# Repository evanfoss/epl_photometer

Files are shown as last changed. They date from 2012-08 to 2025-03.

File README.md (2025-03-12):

# EPL Photometer

By Evan Foss

Date 2011.10.05 (YYYY.MM.DD)

Documentation reuploaded 2025.03.12 by EEF

## Project Description

This project is a photometer, unlike a conventional light meter it is designed to take readings of a stroboscopic light source. It is compact and shielded enough to put in a chamber and operate continuously. It is not meant for perfect for any application because of the limitations in it's response to specific wavelengths and in calibration. It is made with the best matched photodiodes available in our price range. It is also limited in that do to our inability to develop a good reference for single wavelength calibration the device is only good for qualitative (relative) measurements not quantitative measurements. We are working to rectify this last limitation but there is no telling how long it will take to find an adequate calibration method.

# Development

## Toolchain

The development toolchain was as follows:

|Tool Name             | License        | Function
|:---------------      | :------------- | :-----------------
|<a href="https://www.sagemath.org/">SageMath</a>                                            | Open Source       | Scientific Programming Language used for calculations
|<a href="https://github.com/lepton-eda/lepton-eda">lepton-eda</a>                           | Open Source       | EDA (Electronic Design Automation) suite lepton-eda a fork of gEDA
|<a href="http://repo.hu/projects/pcb-rnd/">pcb-rnd</a>                                      | Open Source       | CAD (Computer Aided Design) tool for PCB (Printed Circuit Board) layout gEDA/PCB
|<a href="https://gerbv.github.io/">gerbv</a>                                                | Open Source       | Gerber viewer
|<a href="https://www.gnu.org/software/make/">GNU/Make</a>                                   | Open Source       | Toolchain automation

The project was originally designed using gEDA but Lepton-EDA is backward compatible to it. Like wise the original PCB artwork was designed in gEDA/PCB which was also forked to create pcb-rnd which is also backward compatible.

For the math I was doing I suggest migrating off SageMath to <a href="https://octave.org/">Octave</a> as Sagemath maintence for work this simple is excessive.

## Organization

|File Name/Directory            | Description
|:---------------               |:---------------
|4alberta	                    | The files for the LT1793-sheilded version of the board.
|README.md		                | This file.
|datasheets		                | The data sheets for the various parts used/(considered for use) in the project.
|lt1793-sheilded		        | The 1st production version of the device using an LT1793 for the transimpedance amplifier and a shield using 0.1" spaced headers.
|lt1793-unsheilded	            | The pre-production version of the device using an LT1793 for the transimpedance amplifier minus the shield.
|ltc6240			            | The pre-production version of the device using an LTC6240 for the transimpedance amplifier for higher frequency responce. This design is incomplete.
|math                           | The scripts and calculations used for the design of the device.

## Design

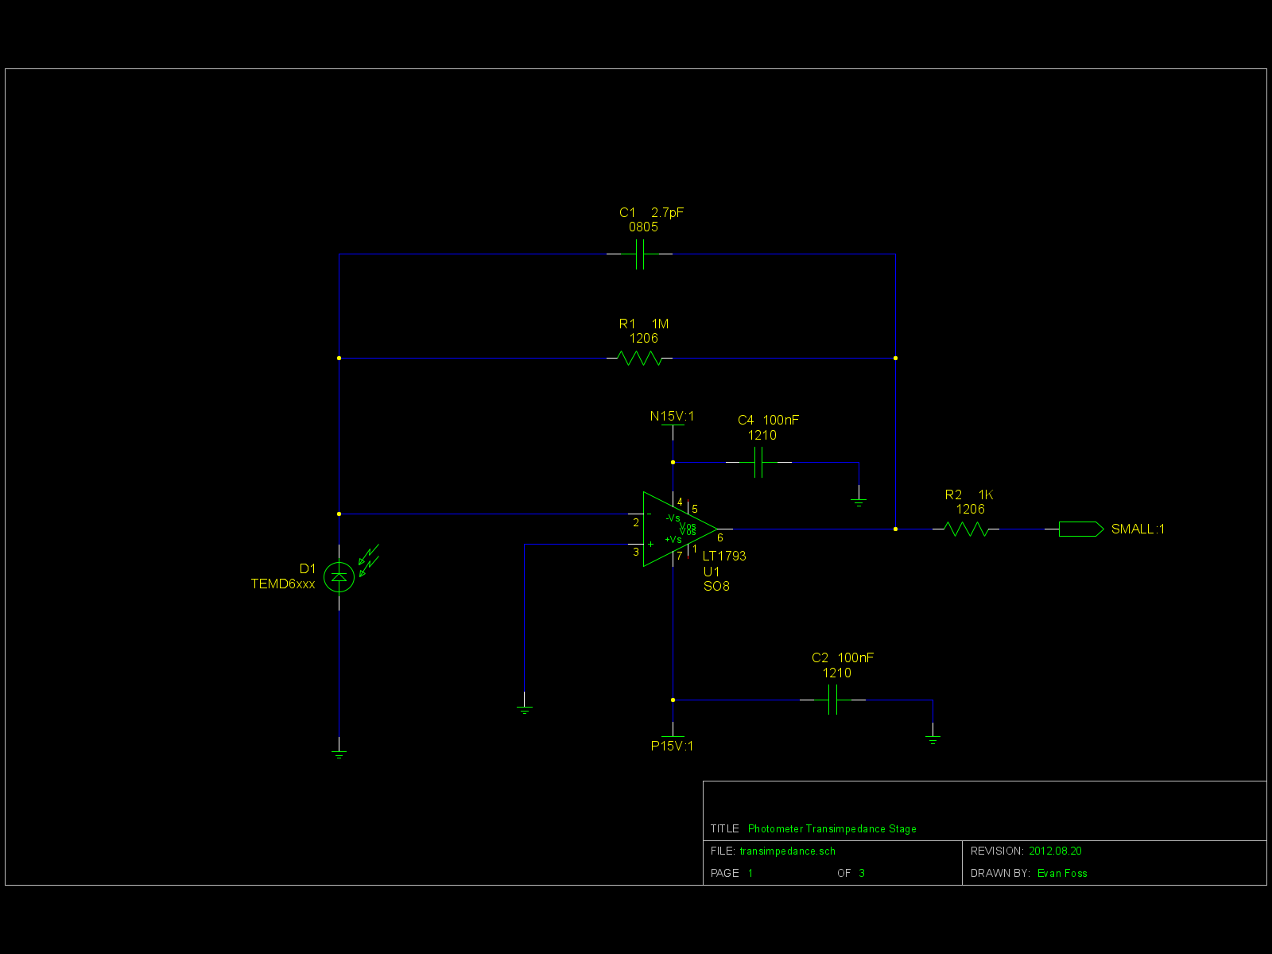
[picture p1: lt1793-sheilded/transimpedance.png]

The photometer uses a photodiode to convert illumination into an electrical current. The current is amplified by a transimpedance stage converting it to a voltage. The voltage is then amplified by a second amplifier that is also capable of driving the capacitive load from the BNC cable. Ideally all the gain would take place in one stage but that is not possible because of real world limitations on the size of the feedback resistor, input capacitance, amplifier stability and etc. More on this will be explained later.

The input diode was selected because it had response in the relevant areas. Many diodes were considered but the TEMD6010FX1 was selected because it had some response in the shorter wavelengths and because it had relatively low capacitance. There were other diodes with more appropriate response but they were all unobtanium because of the minimum quantity required. To carry the project forward we have to assume some things about what the maximum and typical levels of illumination will be. With the amount of illumination the amount of current can be used to work out the required amount of gain for the rest of the device.

The feedback resistor on the transimpedance stage is not large enough on it's own so a second stage is required. The LT1793 was chosen for the transimpedance stage because it has reasonably low input current bias and input current offset which are better for obvious reasons. The LT1793 also has a low input capacitance which is important for stability and just to finish off it has a reasonable gain band width product. For higher bandwidths the LTC6240 was considered but do not need the bandwidth yet. While it is possible to make a larger resistance it would not work because the minor capacitance across the pads of the resistors footprint will be large enough to limit total feedback impedance as frequency increases. While some feedback capacitance is good for compensating the amplifier the effect would be excess role off.

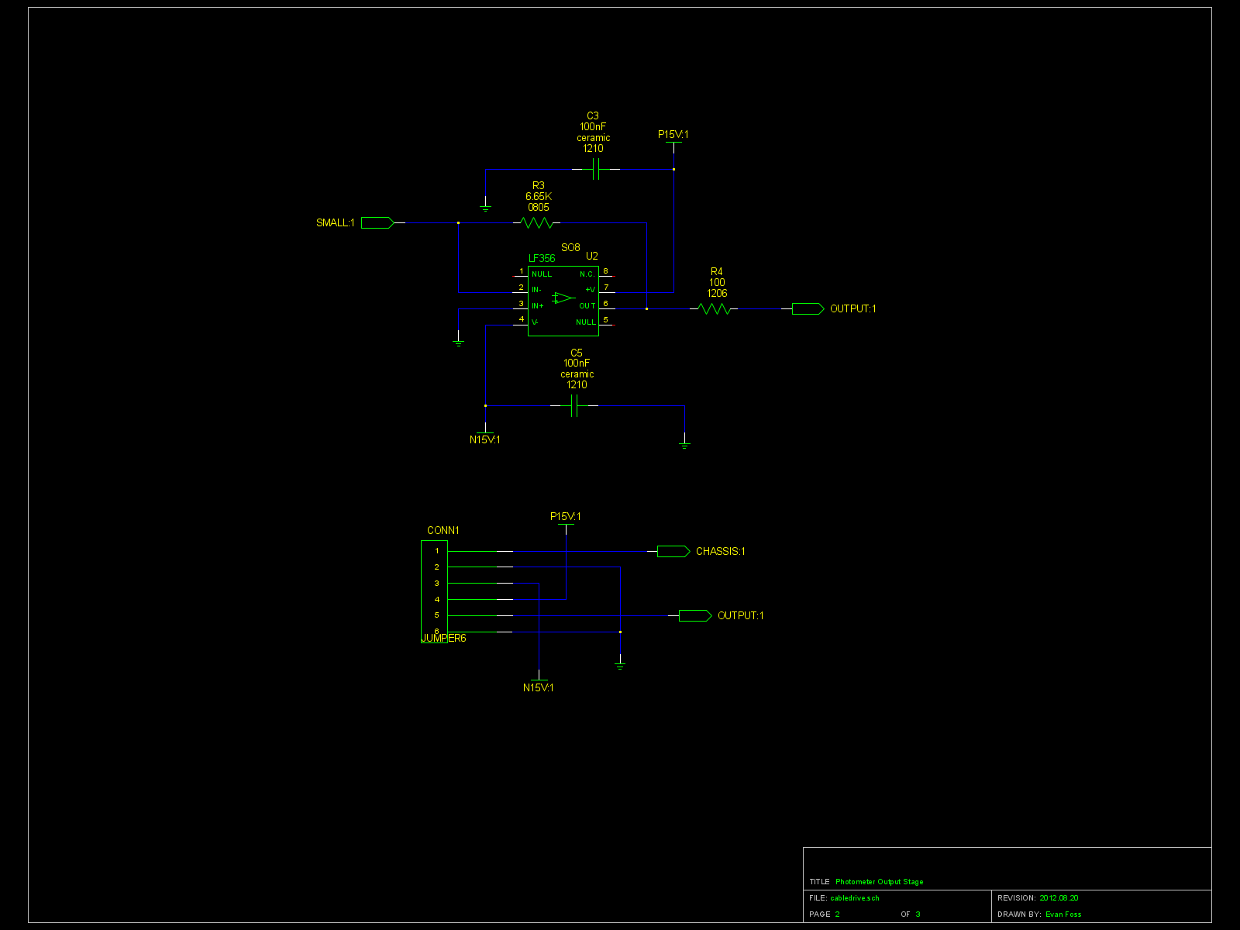
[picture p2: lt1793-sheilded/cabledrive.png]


The second stage is really just meant to pick up the slack from the transimpedance stage and driving the capacitive load of the output cable. It is the ability to drive a capacitive load that is why the LF356 was selected over any number of otherwise comparable amplifiers. The input resistance for the LF356 was selected because it was a reasonable margin from the output current of the LT1793. The math included in the project also checks if there should be a feedback capacitor on the second stage amplifier. It is highly unlikely to be needed.

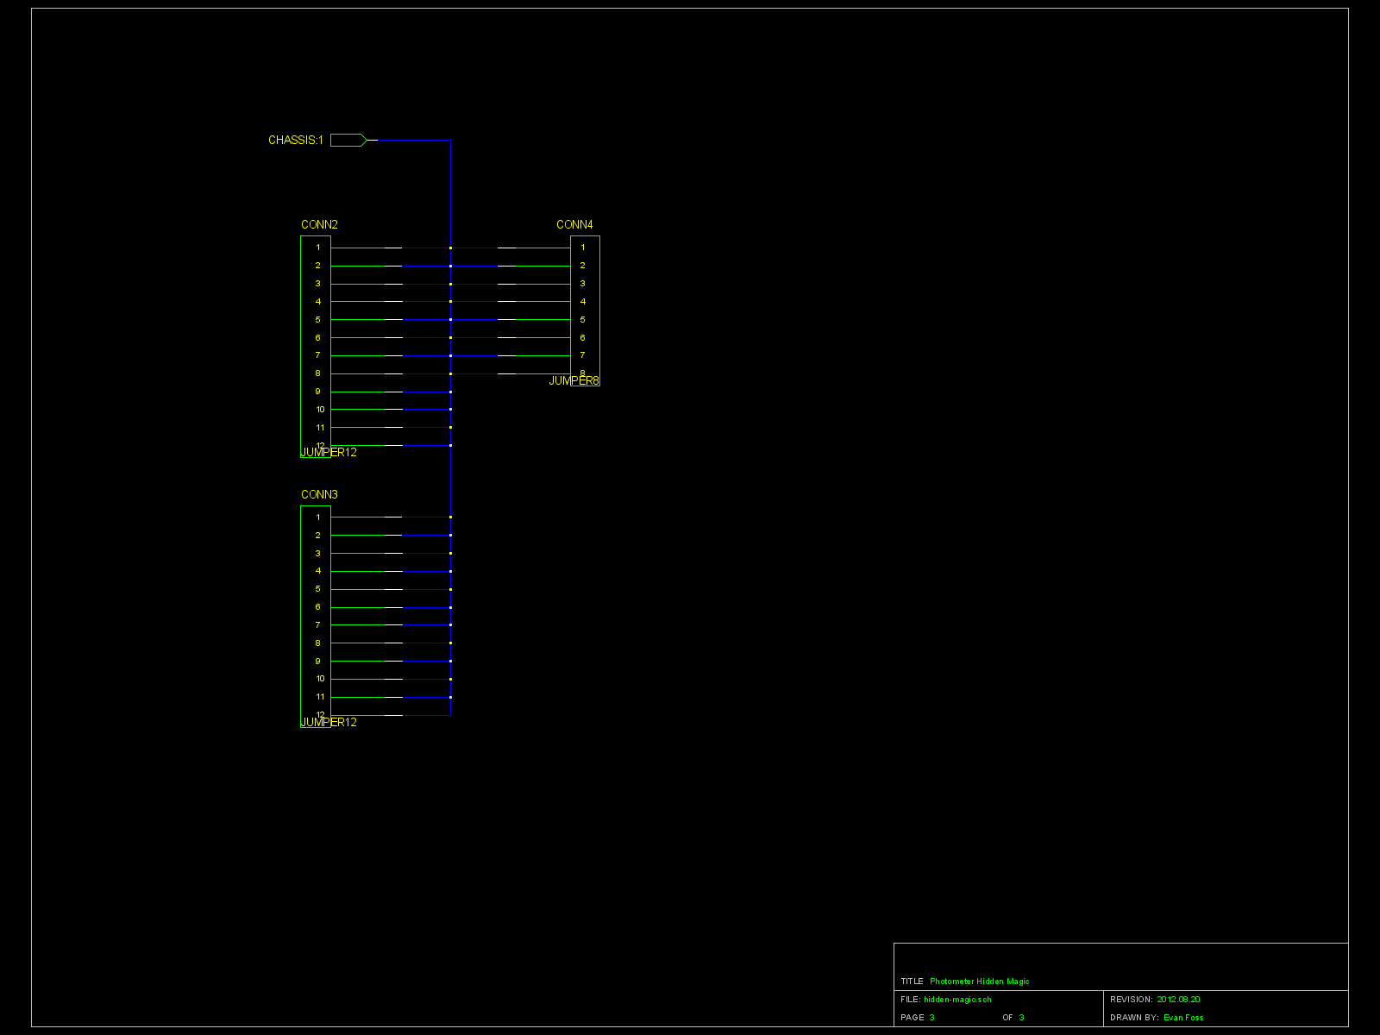
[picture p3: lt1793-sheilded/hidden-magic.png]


This is just the shielding for the device. Transimpedance amplifiers are very noise sensitive.

# Construction

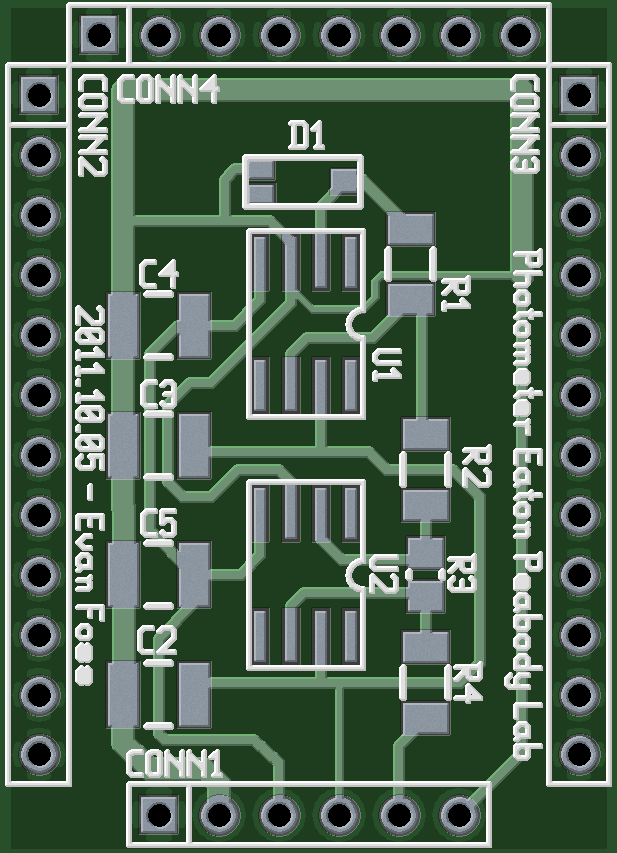
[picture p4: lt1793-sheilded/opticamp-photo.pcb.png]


The construction of the photometer seems straight forward until you consider the troubles of making it compact with only 2 layers for cost reasons and only 1 layer used for the design because the bottom is going to be used as part of the shield. The whole design except for the connector and the shield is done in SMT. 

Doing the shield in SMT was considered but that would have meant using a sheet of brass or copper and soldering it directly to the back layer of the board. While this is possible it would make rework on the board difficult and it would put considerable thermal stress on the board. The pads such a shield would have needed would have been of considerable size and the heat used to solder them might have cause them to delaminate off the board substraight. The  photodiode needs to be exposed for the best results but it also must be on the board to reduce capacitance so there is a whole in the shield. It has been our experience that holes attract all manner of unwanted contaminants so the shield needs to be removable for cleaning. It adds a considerable mount of bulk but 0.100” headers are used to connect the shield to the board. The shield being a piece of perforated board with a ground plane on it soldered to the headers.

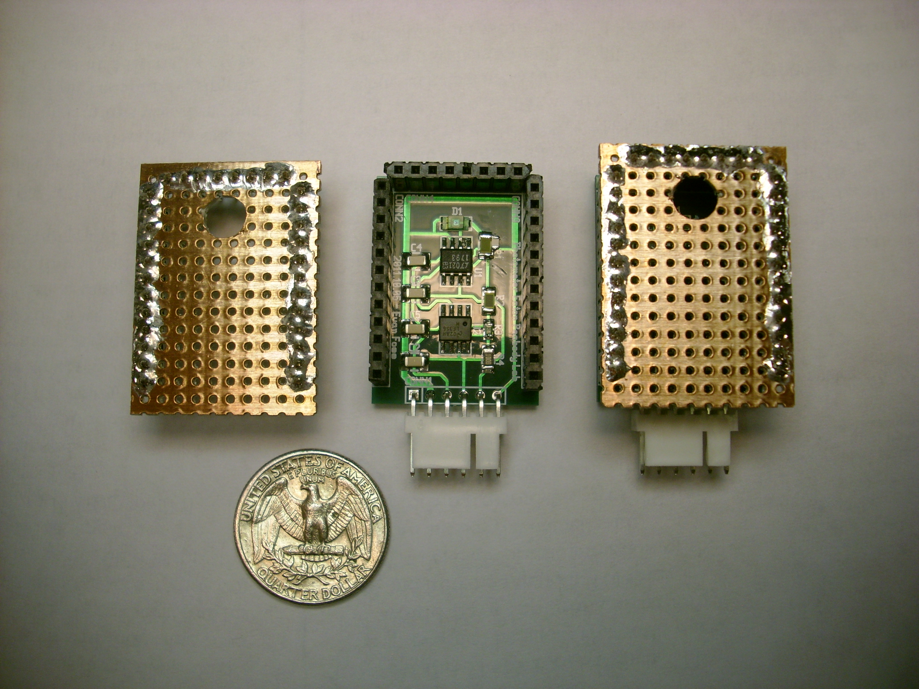
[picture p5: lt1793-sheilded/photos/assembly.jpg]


While the space between the transimpedance amplifier and the output stage amplifier is not that critical many other areas are very tightly controlled. The space between the photodiode and the trans-impedance amplifier should be as short as possible to reduce trace capacitance. The distance between the feedback resistors and their accompanying amplifiers also have to be kept short. The input resistor on the output amplifier is not very controlled and given the small size of the whole space the distance between the decoupling capacitors and everything else is also with in reason not critical. 

Making the connector in SMT was considered but having the connector pins go threw the board helps mechanically if the connector sees excess torc which can happen. The downside is of course that those points are exposed to the outside and could introduce noise but if this is a problem a small bit of adhesive backed copper foil can be put over the clip side of the connector or indeed the whole mating area.

To get from the connector on the photometer to the rest of the world there are two different methods. In a chamber the device uses a shielded cable carrying both the power and signal lines to an PCB with and edge card connector. The edge card supplies power from our standard EPL configuration of the EFP series vector subrack. The signal comes out of that same board via a right angle BNC connector. In the second configuration we use two shielded cables on going to a MiniHEX9 for power and the other to a BNC connector for the signal output. Because of the outside of the BNC cable being only at analog ground and not at shield potential this version is not suitable for use in a chamber.

# Validation

The photometer was tested for it's frequency reponse, noise floor, and linearity.

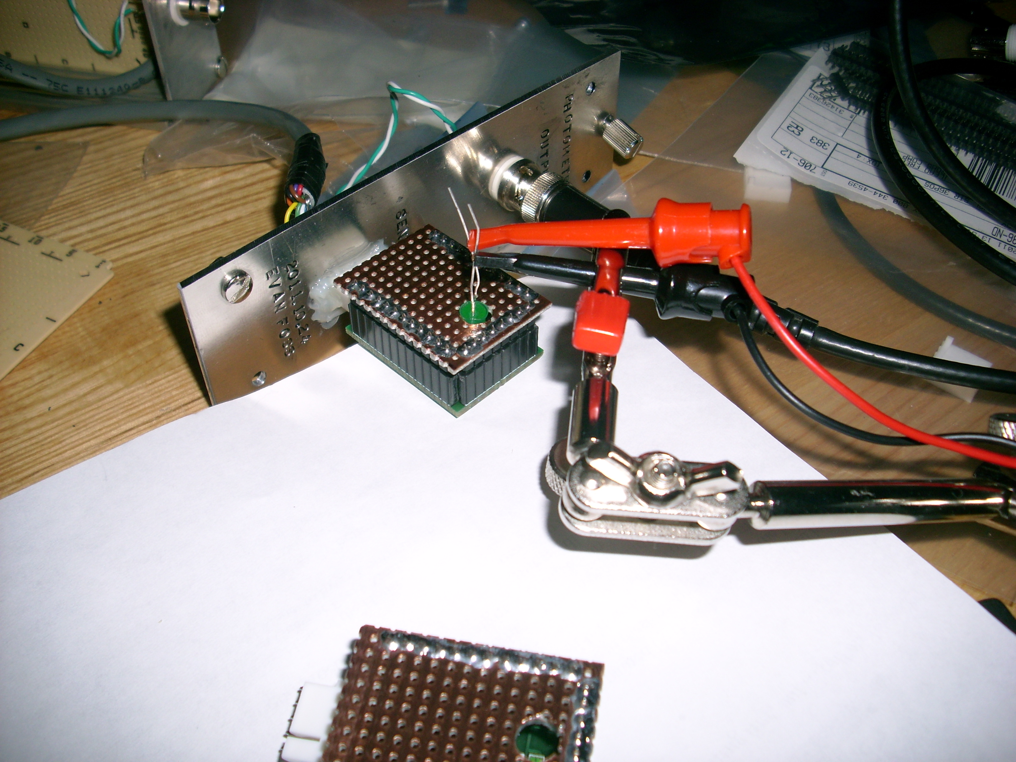
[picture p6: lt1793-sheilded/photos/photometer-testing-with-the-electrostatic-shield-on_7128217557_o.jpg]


For more on that testing data reach out to who ever has my lab notebook now.

|Generator used|Fall Time|Rise Time|Linearity
|:---------------|:---------------|:---------------|:---------------
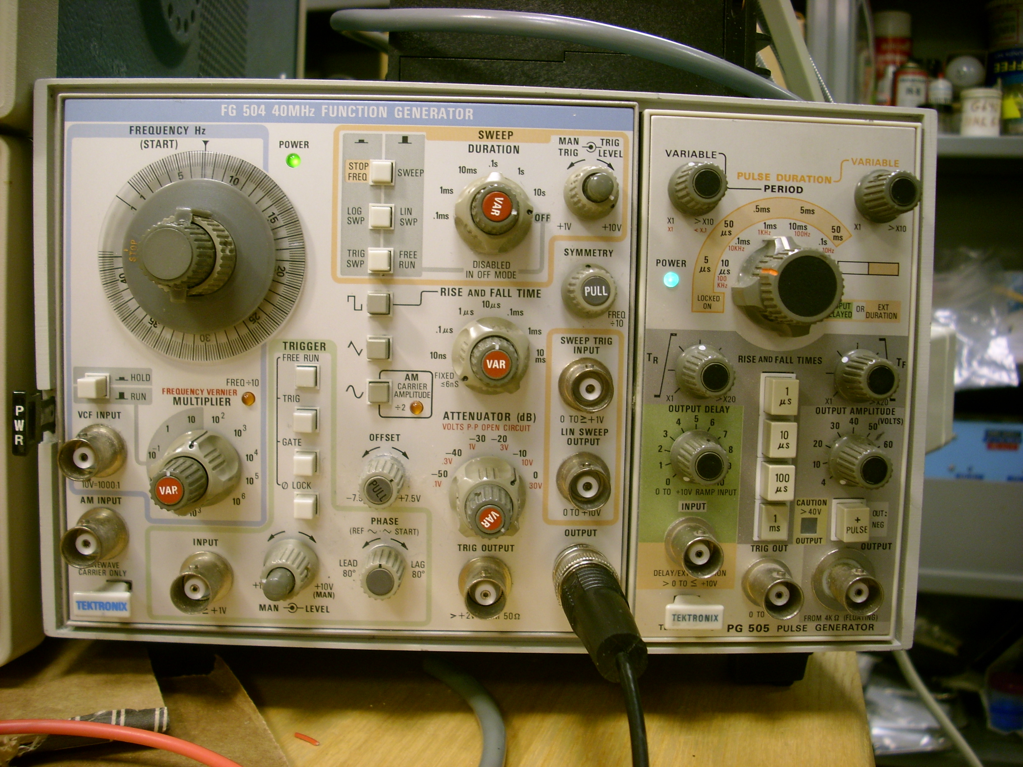
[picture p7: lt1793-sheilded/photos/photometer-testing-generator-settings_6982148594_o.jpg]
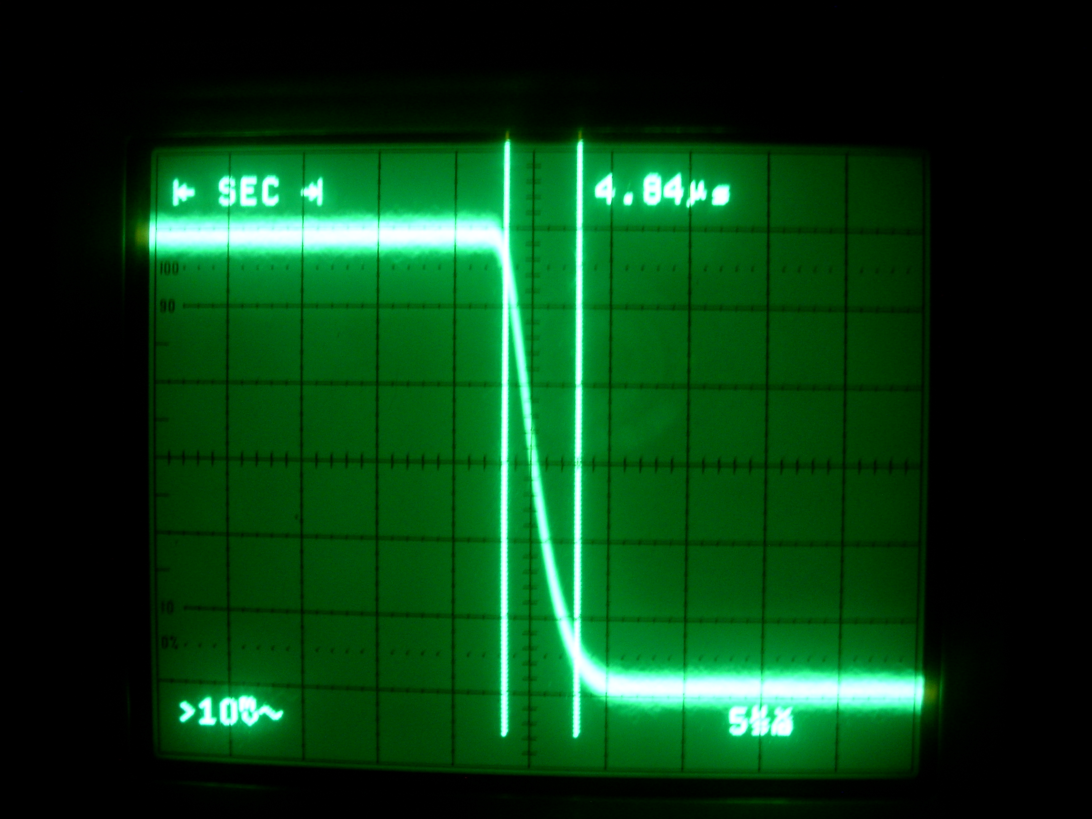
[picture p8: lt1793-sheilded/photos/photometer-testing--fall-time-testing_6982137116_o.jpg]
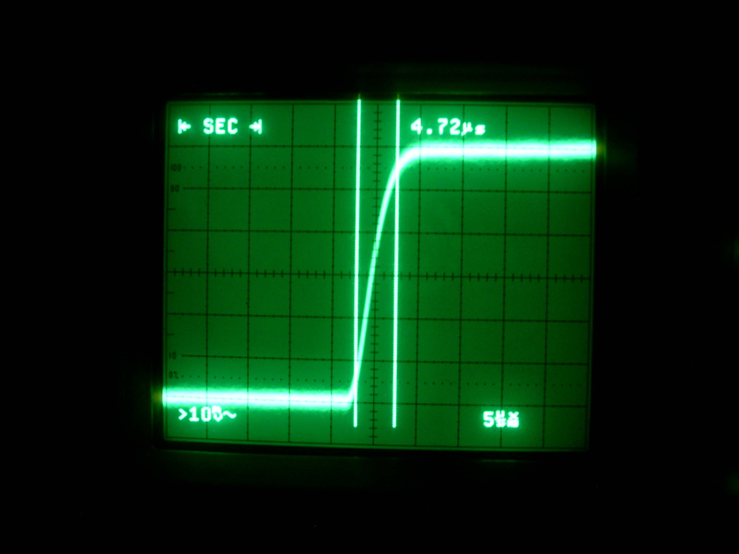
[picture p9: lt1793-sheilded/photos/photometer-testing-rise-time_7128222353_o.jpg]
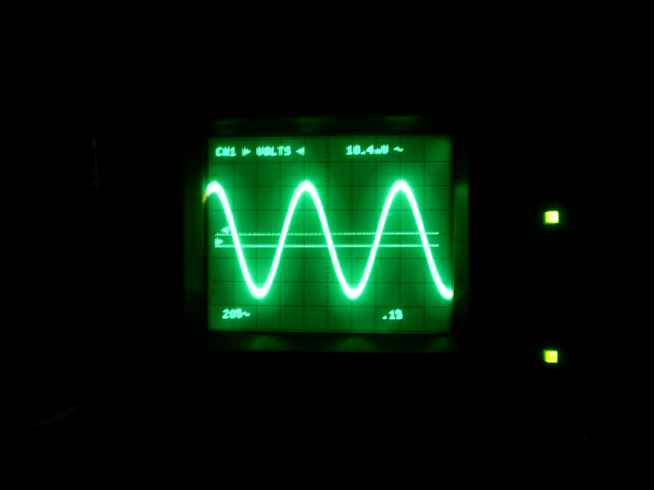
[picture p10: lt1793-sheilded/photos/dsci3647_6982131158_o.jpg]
||||

# Future

We only have to needs from this device that are unfulfilled. First we would like to be able calibrate it to a source of a known wavelength and power. Second it would be nice if it could have a better response at smaller wavelengths. Sadly we do not have the resources at this point but that may change later.

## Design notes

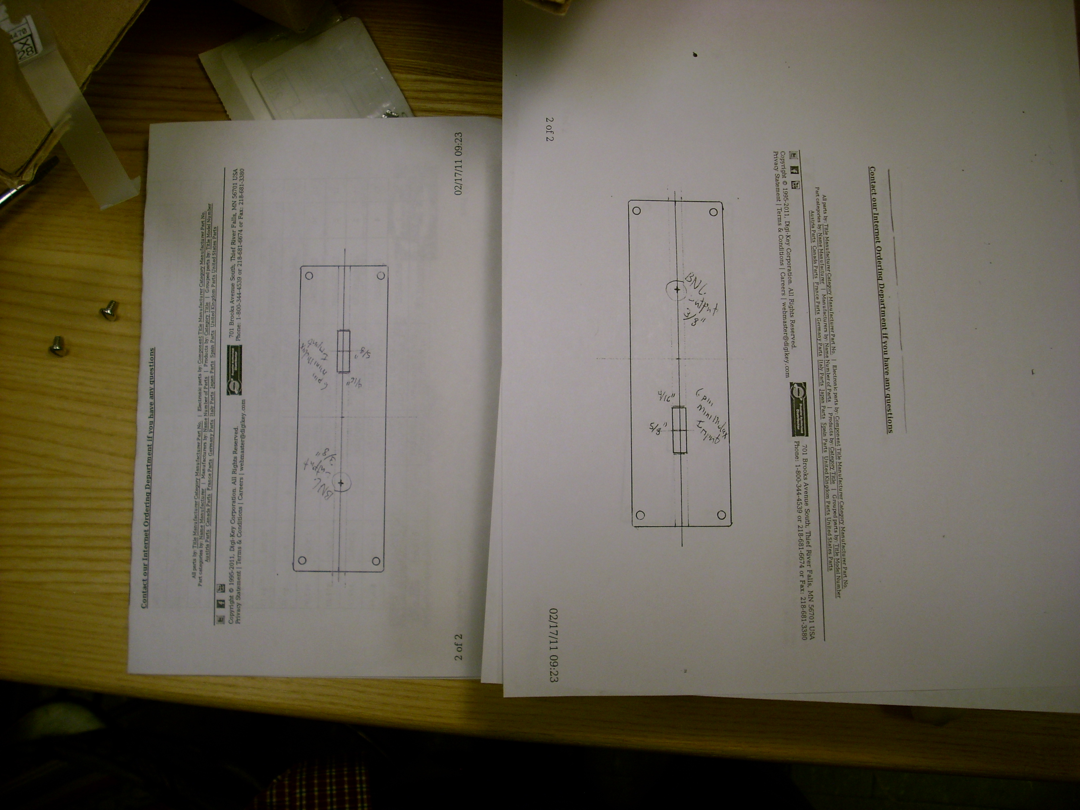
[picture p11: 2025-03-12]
lt1793-sheilded/photos/photometer--front-panel-design_6982178266_o.jpg

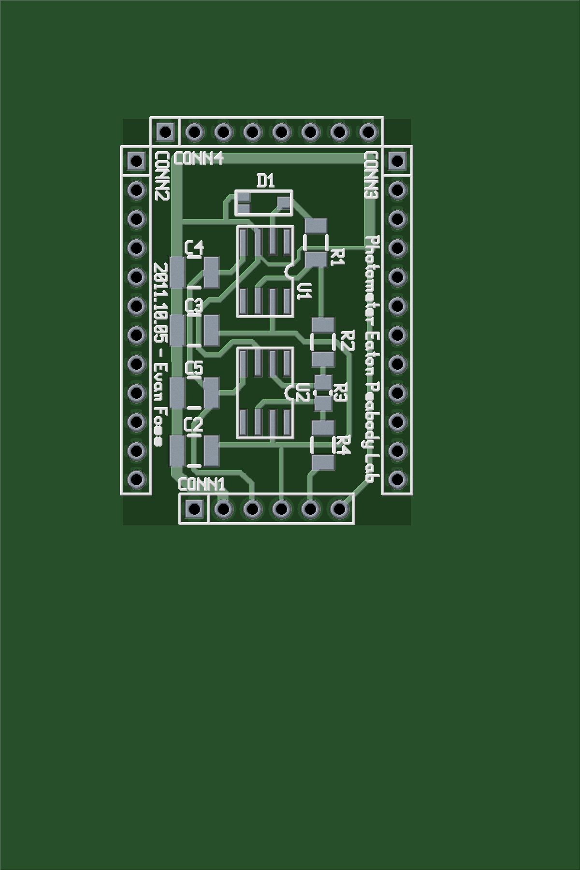
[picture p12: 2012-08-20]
lt1793-sheilded/opticamp.png.png

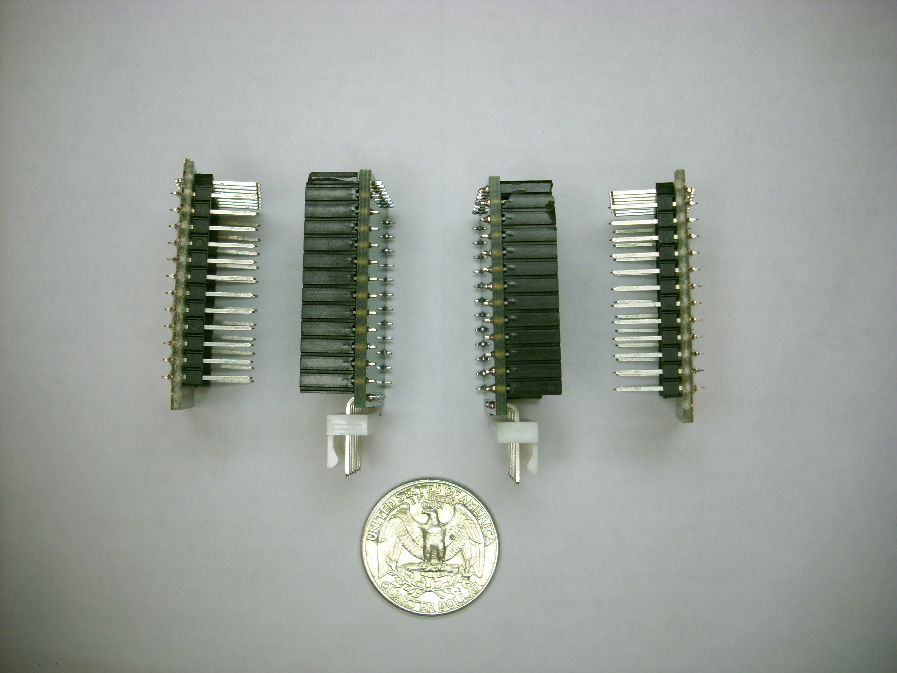
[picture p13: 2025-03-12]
lt1793-sheilded/photos/dsci3637_7128222995_o.jpg

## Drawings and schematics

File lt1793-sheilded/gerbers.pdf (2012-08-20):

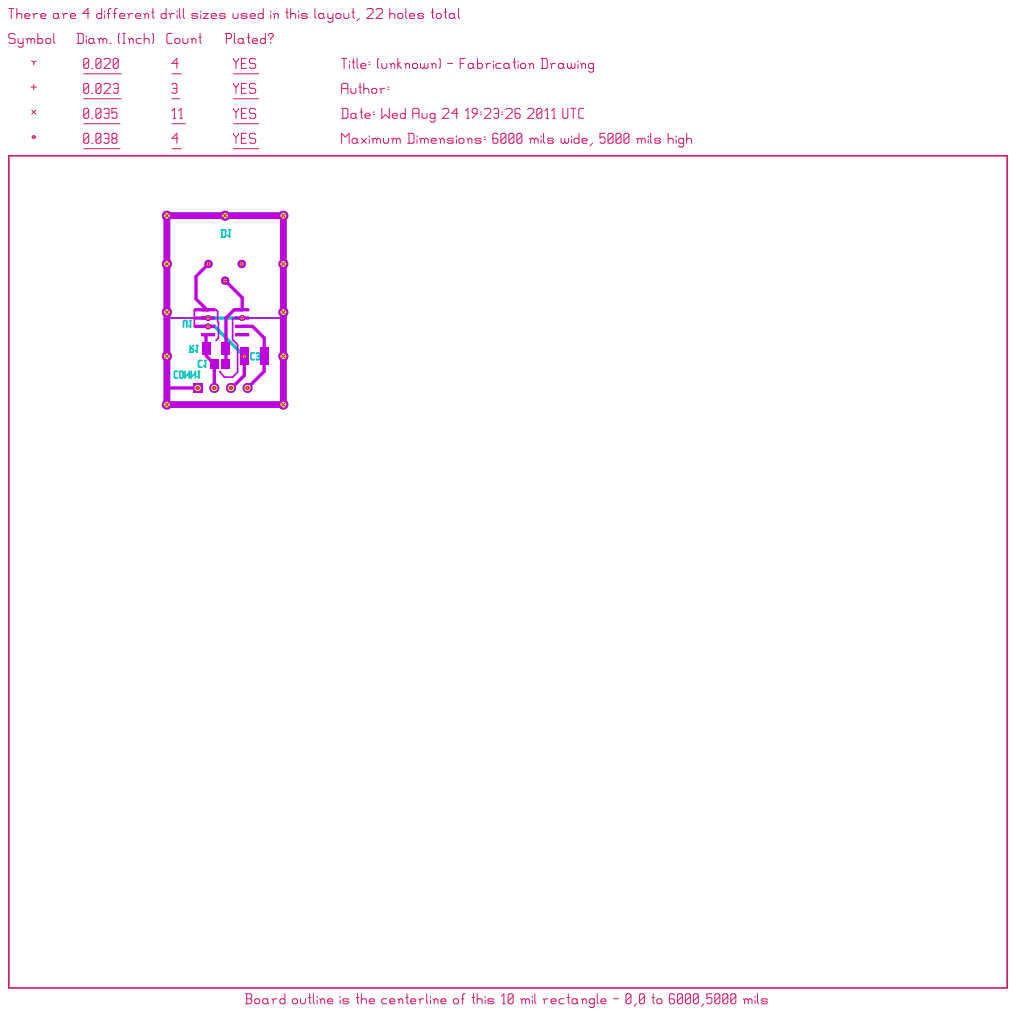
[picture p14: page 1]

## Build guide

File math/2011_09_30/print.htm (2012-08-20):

jsMath

# EPL-Photometer4AnnHickox_and_PingXi

#Project: EPL_Photometer #By: Evan Foss #Date: 2011.09.08 #Description: #Ann needs a photometer that will meter white light as mice perceive it. #Their range is from Green (560nm) to UV (unknown). #The response time is in the 1msec or better. #The output voltage is from 0V to 10V peak. #The output must be linear to the light in. # #Ping needs a photometer that will do basically the same but she needs it to #operate in 474nm to 480nm. # #Basically the project this worksheet is a spinoff of the one for the #fiber-optic microphone amplifier. Only that project ended before I finished #all the math.

#Define some Scale femto = 10^(-15) pico = 10^(-12) nano = 10^(-9) micro = 10^(-6) mili = 10^(-3) deci = 10^(-1) Deca = 10^1 Kilo = 10^3 Mega = 10^6 Giga = 10^9

#DAQ Spec. #Input Voltage Peek (absolute) DAQ_Vpeekabs = 10

#Diode Model (TEMD6010FX01) #diode capacitance varies on model but 15pF would seem to be the max. D1photo_C = 60*pico #Peek Current D1photo_Ipeek = 3*micro #What is the D1photo_Itypical = 300*nano

#opamp spec. (LT1793) #current noise (it will actually be less than this because this is at 1KHz) U1OpAmp_InInoise = 1*femto #Gain Bandwidth Product U1OpAmp_GBW = 4.7*Mega #What is the common mode input capacitance U1OpAmp_InCcom = 1.5*pico #Supply Current U1OpAmp_Isupply = 4.2*mili #What is the max voltage the opamp can deliver? #This is not the true max. output voltage only the most I want to use to limit total harmonic distortion. U1OpAmp_OutVmax = 2.75

#opamp spec. U2 (LF356) #Gain Bandwidth Product U2OpAmp_GBW = 5*Mega #Input Capacitance U2OpAmp_Cinput = 3*pico #Supply Current U2OpAmp_Isupply = 5*mili

#What is the minimum target bandwidth of the whole amplifier? Responce_time_min = 1*mili BW_min = 1/Responce_time_min #BW = 30*Kilo BW = BW_min*(5+1/3) print "Band Width (min) =", float(BW_min/Kilo), "KHz" print "Band Width (target) =", float(BW/Kilo), "KHz" #What is the amount of gain required for optimal performance in the first stage? U1OpAmp_ClosedLGain = U1OpAmp_OutVmax / D1photo_Ipeek print "What is the ideal transimpedance gain =", float(U1OpAmp_ClosedLGain)

| Band Width (min) = 1.0 KHz Band Width (target) = 5.33333333333 KHz What is the ideal transimpedance gain = 916666.666667

#what is the impedance inside the photodiode (and opamp inputs) at that level? Input_CreactanceBW = 1/(2*pi*BW*(D1photo_C + U1OpAmp_InCcom)) print "Input Reactance at 3DB point =", float(Input_CreactanceBW), ""

| Input Reactance at 3DB point = 485228.485036

#so the output voltage noise will be... U1OpAmp_OutVnoise = U1OpAmp_InInoise * Input_CreactanceBW print "Projected noise from opamp input current noise and photo diode reactance =", float(U1OpAmp_OutVnoise/nano), "nV"

| Projected noise from opamp input current noise and photo diode reactance = 0.485228485036 nV

print "That should be around 0.8fA/sqrt(Hz) which matches the LT1793 data sheet."

| That should be around 0.8fA/sqrt(Hz) which matches the LT1793 data sheet.

print "I do not like actually using 916KOhms because using parallel resistors will add parallel copper on the PCB." print "The extra trace capacitance from that would further limit the size of the feedback resistor." print "I know that going up to 1MOhm will only be a small change."

| I do not like actually using 916KOhms because using parallel resistors will add parallel copper on the PCB. The extra trace capacitance from that would further limit the size of the feedback resistor. I know that going up to 1MOhm will only be a small change.

#What is the feedback resistor for the first stage? R1_feedback = 1*Mega C1_feedback = sqrt((D1photo_C + U1OpAmp_InCcom) / (U1OpAmp_GBW*2*pi*R1_feedback)) print "The feedback capacitor should be =", float(C1_feedback/pico), "pF"

| The feedback capacitor should be = 1.44310753644 pF

#Only that calculation is rubbish because I will likely get at least 1pF from the artwork on the PCB. #This means that I will have to use less feedback resistance and more feedback capacitance. #The above work will have to be redone using Cfeeback as the limiting factor for Rfeedback and not the #other way around.

#Now that we know C_feedback needs to be the limiting factor what should it be... #I am going to figure the board to have < 5pF of capacitance and I know that the #smallest value capacitor I can get in decent tolerance is 4.7pF. C1_feedback = 1.5*pico #Now a little algerbra #C_feedback = sqrt(Dphoto_C / (OpAmp_GBW*2*pi*R_feedback)) #C_feedback^2 = Dphoto_C / (OpAmp_GBW*2*pi*R_feedback) #C_feedback^2 / Dphoto_C = 1 / OpAmp_GBW*2*pi*R_feedback #(C_feedback^2 * OpAmp_GBW*2*pi) / Dphoto_C = 1 / R_feedback #R_feedback = Dphoto_C / (C_feedback^2 * OpAmp_GBW*2*pi) R1_feedback = (D1photo_C + U1OpAmp_InCcom) / (C1_feedback^2 * U1OpAmp_GBW*2*pi) print "The largest Rfeedback can be is =", float(R1_feedback/Kilo), "KOhms"

| The largest Rfeedback can be is = 925.581938549 KOhms

#The ideal feedback resistor is just a little off from what is actually available. R1_feedback = 1*Mega

#With the feedback resistor and feedback capacitor worked out I can calculate the peek output voltage for the transimpedance stage. V_transimpedancePeek = D1photo_Ipeek*R1_feedback print "Voltage out of Transimpedance (@peek) =", float(V_transimpedancePeek), "V"

| Voltage out of Transimpedance (@peek) = 3.0 V

#What is the ideal gain for the output amplifier? U2OpAmp_ClosedLGain = (DAQ_Vpeekabs / V_transimpedancePeek) print "Gain (stage2) =", float(U2OpAmp_ClosedLGain)

| Gain (stage2) = 3.33333333333

#What is the ideal input resistor for the second stage. #I always prefer to add 1/3rd to the output resistor to reduce the current output from the transimpedance stage. R2_input = (V_transimpedancePeek / U2OpAmp_Isupply)*(1+1/3) print "Input resistor ideal (2ndstage) =", float(R2_input), "Ohms"

| Input resistor ideal (2ndstage) = 800.0 Ohms

#Heck with that I am just going to round it up... R2_input = 1*Kilo print "Input resistor (2ndstage) =", float(R2_input/Kilo), "KOhms" #What is the ideal feedback resistor R3_feedback = U2OpAmp_ClosedLGain * R2_input print "Feedback resistor ideal (2ndstage) =", float(R3_feedback/Kilo), "KOhms" R3_feedback = 3.32*Kilo print "Feedback resistor selected (2ndstage) =", float(R3_feedback/Kilo), "KOhms"

| Input resistor (2ndstage) = 1.0 KOhms Feedback resistor ideal (2ndstage) = 3.33333333333 KOhms Feedback resistor selected (2ndstage) = 3.32 KOhms

#Will this combination come close to the target output at full scale? U2_VOutPeek = V_transimpedancePeek * (R3_feedback / R2_input) print "What is the peek voltage output (2ndstage) =", float(U2_VOutPeek), "V" print "That should give a fair amount of leeway for the resistor tolerances."

| What is the peek voltage output (2ndstage) = 9.96 V That should give a fair amount of leeway for the resistor tolerances.

#U2 source capacitance (assumed to mostly be from board impedance) U2OpAmp_CSource = 1.5*pico #What is the frequency of the pole formed by U2's input capacitence U2OpAmp_Rparallel = (R3_feedback * R2_input) / (R3_feedback + R2_input) U2OpAmp_Fpole = 1 / (2 * pi * U2OpAmp_CSource * U2OpAmp_Rparallel) print "U2 frequency pole (Uncompensated) =", float(U2OpAmp_Fpole/Mega), "MHz" if (U2OpAmp_Fpole < 6 * BW) : print "You should add a feedback capacitor to U2." if (U2OpAmp_Fpole <= 10 * BW and U2OpAmp_Fpole >= 6 * BW) : print "You may consider adding a feedback capacitor to U2." if (U2OpAmp_Fpole > 10 * BW) : print "You probably do not need a feedback capacitor."

| U2 frequency pole (Uncompensated) = 138.062119309 MHz You probably do not need a feedback capacitor.

#Low frequency noise gain #The following is from the LMC662 datasheet U2OpAmp_GainLowFrequency = 1 + R3_feedback / R2_input

#Theoretical feedback capacitor if (U2OpAmp_GainLowFrequency >= 2*sqrt(U2OpAmp_GBW * R3_feedback * (U2OpAmp_CSource + U2OpAmp_Cinput))) : C2_feedback = (U2OpAmp_CSource + U2OpAmp_Cinput) / (2 * (1 + R3_feedback / R2_input)) if (U2OpAmp_GainLowFrequency < 2*sqrt(U2OpAmp_GBW * R3_feedback * (U2OpAmp_CSource + U2OpAmp_Cinput))) : C2_feedback = sqrt((U2OpAmp_Csource + U2OpAmp_Cinput) / (U2_GBW * R3_feedback)) if (C2_feedback >= 10*pico or U2OpAmp_Fpole <= 6 * BW) : print "U2 feedback capacitor =", float(C2_feedback/pico), "pF" if (C2_feedback < 10*pico and U2OpAmp_Fpole > 10) : print "C2 (feedback capacitor on U2) is not needed but remember the reference designator C2 is reserved."

| C2 (feedback capacitor on U2) is not needed but remember the reference designator C2 is reserved.

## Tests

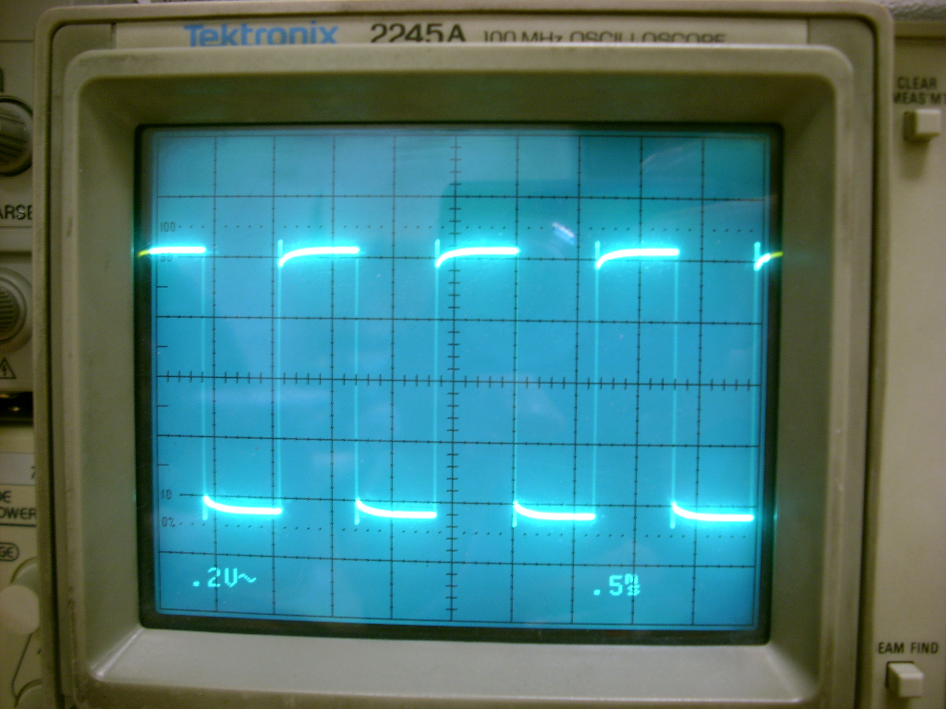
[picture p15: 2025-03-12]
lt1793-sheilded/photos/photometer-testing-pre-calibration-overshoot_6982148132_o.jpg

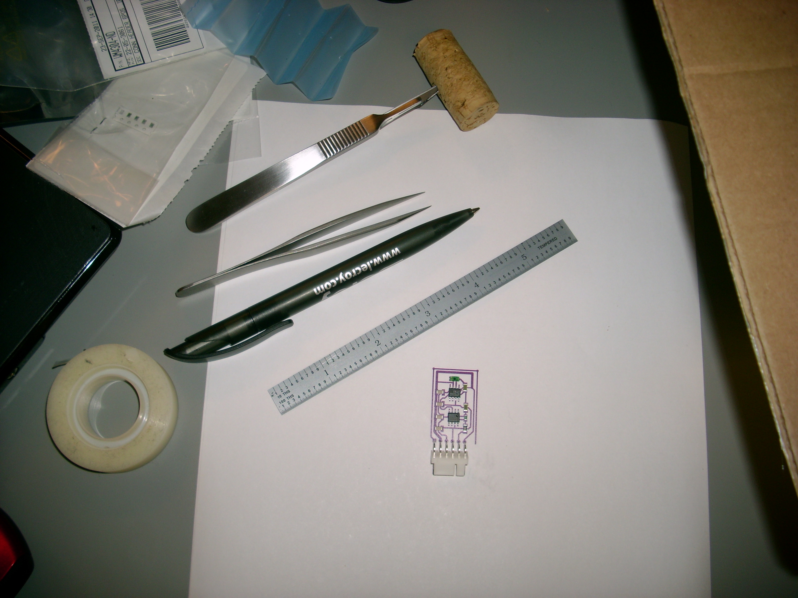
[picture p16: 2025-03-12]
lt1793-sheilded/photos/epl-photometer-footprint-testing_6466402671_o.jpg

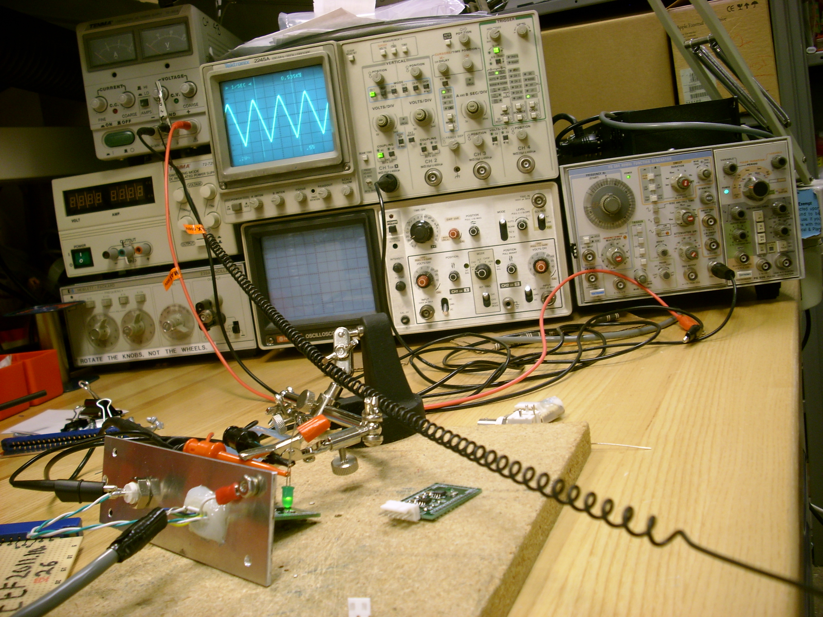
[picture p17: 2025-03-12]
lt1793-sheilded/photos/photometer-testing-sawtooth_6982150026_o.jpg

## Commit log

2012-08-20 Initial release lt1793-sheilded is the 1st verion
    [amplifier.sch, cabledrive.sch, cmsk.gbr, compont.gbr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]
2012-08-20 Fixed title blocks.
    [cabledrive.sch, hidden-magic.sch, transimpedance.sch]
2012-08-20 Fixed incorrect depection of the shield.
    [transimpedance.sch]
2012-08-22 Fixed BOM in schematic by copying model attribute to value attribute on semi and conn refdes.
    [cabledrive.sch, transimpedance.sch]
2012-08-22 Changed board capacitence across feedback resistor to the actual feedback capacitor I had to add for stability.
    [transimpedance.sch]
2025-03-12 fix: better pcb rendering
2025-03-12 add: actual assembly photo
2025-03-25 add: changed to more modern tools lepton-eda and pcb-rnd
